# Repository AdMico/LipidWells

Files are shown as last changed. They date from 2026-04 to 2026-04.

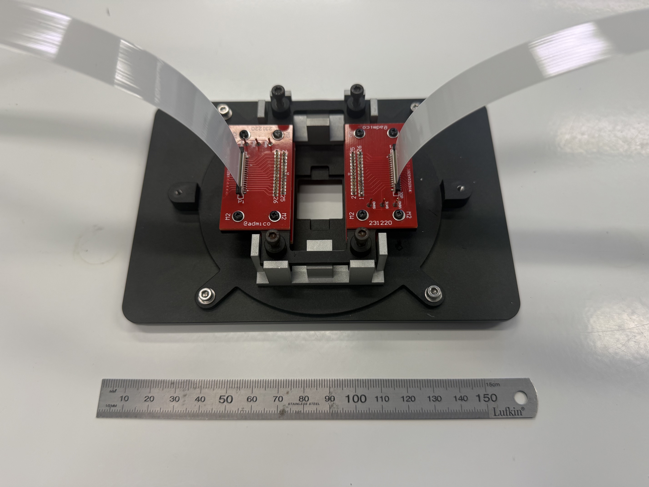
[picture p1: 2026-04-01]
CNC Parts/Stage Parts/Stage_Assy_2.jpeg

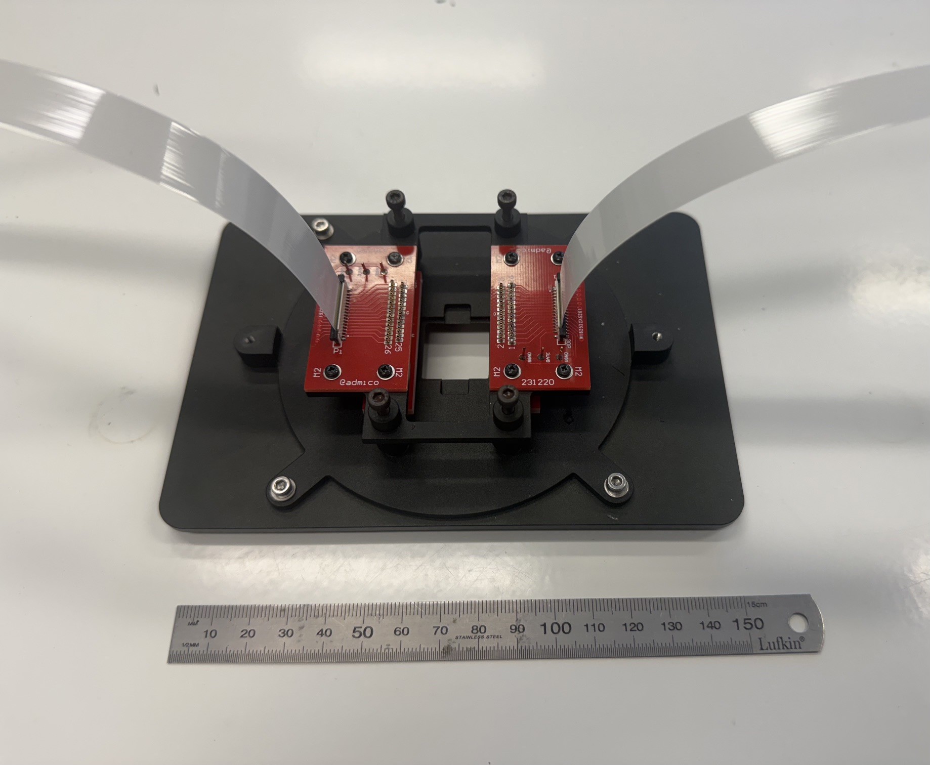
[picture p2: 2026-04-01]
CNC Parts/Stage Parts/Stage_Assy_1.jpeg

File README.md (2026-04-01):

# LipidWells v1.0.0 (Updated 01APR26 APM)

**Written by:** Adam Micolich

**Purpose:** Hardware aspects related to our work on 'Organic Electrochemical Transistor Arrays with Integrated Lipid-Sealed Femtolitre Chambers for Simultaneous Electrical and Optical Detection of Membrane Protein Activity'

## Structure

The top level has three folders -- *CNC Parts*, *PCBs & Schematics* and *Photomasks*.

The *CNC Parts* folder has two sub-folders -- *MUXBox*, which contains all the panels for the multiplexer box, and *Stage Parts*, which has all the various components for mounting a coverslip onto a microscope and making the electrical connections to that coverslip.

The *PCBs & Schematics* folder contains five sub-folders which have the PCB designs, Schematics (as appropriate) and the Gerber file sets for production for the six different PCBs used in this project. It also contains a parts list for all the additional components needed for completing the multiplexer box and associated PCBs.

The *Photomasks* folder contains a PDF file with some extended notes about the respective photomask designs.

The photomask files are hosted as a release due to the large file size involved. The photomask release contains 5 compressed RAR files, which contain the GDSII files for production of the photomasks used in this project, with a download size of 238MB (n.b., some of the files, uncompressed, are nearly 1GB in size due to the huge number of components in the design).

Each of the three folders above has its own `README.md` file with further details regarding the contents of those folders.

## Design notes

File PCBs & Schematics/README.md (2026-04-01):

# LipidWells v1.0.0 (Updated 01APR26 APM)

**Written by:** Adam Micolich

## Contents of the *PCBs & Schematics* folder

There are five folders, the contents of these folders are as follows:

*Drill Board*: This is the PCB for the pair of boards that mount on the bottom of the Pinplate and sit either side of the nodule on the Harwin spring-pin sleeve to set the height of the spring-pins on the Pinplate assembly. There is a PDF file showing the PCB design to actual size, along with a folder containing all the Gerber files needed to have this PCB produced. There is no metal on this board, all it has is drill holes, soldermask and silkscreen.

*MUX Board*: This is the PCB that has all the circuitry for multiplexing the measurement instruments to the devices on the coverslip. I will describe it in more detail in the notes in the next section. There is a photograph of an Assembled MUX Box for reference in building one, along with a PDF file showing the PCB design to actual size, a PDF file showing the schematic diagrams for the circuit, and a folder containing all the Gerber files needed to have this PCB produced. It is a fairly standard two-layer PCB.

*Pin Breakout Board*: This is the PCB that mounts on the top of the Pinplate and which connects the 27 Harwin spring-pins on each side to a corresponding 30-pin ribbon cable. A photograph of a completed version of this PCB, as mounted on the Pinplate, can be found in the *Stage Parts* sub-folder of the *CNC Parts* folder. There is a PDF file showing the PCB design to actual size, a PDF file showing the schematic diagram for the circuit, and a folder containing all the Gerber files needed to have this PCB produced. It is a fairly standard two-layer PCB.

*Sidepanel Board*: This is a PCB that mounts in the left wall of the MUX Box and which acts as a feedthrough for the two 30-pin and one 40-pin ribbon cables from inside to outside the box. There is a PDF file showing the PCB design to actual size, a PDF file showing the schematic diagram for the circuit, and a folder containing all the Gerber files needed to have this PCB produced. It is a fairly standard four-layer PCB, designed to maintain the ground-screening of the left-box wall as much as practicable (in hindsight, perhaps overkill, but interesting to convince myself it could be done should it ever be required for measurements where the signal-to-noise ratio is more difficult that it was in this experiment).

*Test Device Board*: There are actually two PCBs in this folder, which are slight variants of each other. The intention is to make a PCB that can act as a 'dummy device' for testing the electronics/software, without needing to use device coverslips. The 'single' version has a pair of resistors, one for each 'side' of the device, that give a common value on all lines during testing. We invariably always put a 1K, 3K or 10K resistor in here for both positions. The 'multi' version is designed to look more like a real device, in that different lines give slightly different values, and we put a random selection of 2.7K, 3.0K and 3.3K resistors into the 26 SMD resistor positions on this test board. In both cases there is a PDF file showing the PCB design to actual size, and a folder containing all the Gerber files needed to have these PCBs produced. It is a fairly standard two-layer PCB.

We get these PCBs made for us by PCBWay in China.

## Brief discussion of the circuit design aspects for the MUX Box

The schematic for the Mux Board has two sheets, one for the power circuit and one for the signal circuit.

The signal circuit is designed to interface the 60-lines going to the coverslip (54 device lines plus 6 extra lines for ground and gate voltage) to the four BNC connectors that are connected to the analog outputs (AO0/AO1) of the National Instruments USB-6216-BNC and the inputs of the two Femto DLPCA-200 current pre-amplifiers. The switching is performed by a set of four Analog Devices MAX306 16-channel CMOS multiplexer ICs, a pair for each of the 30-pin ribbon cables, that are bit-controlled by the GPIO lines of the Raspberry Pi included in the setup. They are powered by +/-15V rails to minimise the resistance contribution that they make to the measurement lines.

The power circuit is designed to provide the +/-15V supply for the multiplexers. For noise reasons, we elected to do this using a set of four 9V batteries, which provide up to 18V either side of ground. The batteries are split into positive (2 x 9V) and negative (2 x 9V) banks, each of which connect to a DPDT toggle switch on the MUXBox top panel. This switch in the left-hand position connects the batteries to the upper part of the circuit diagram in the schematic, which is a circuit to 'clean-up' the voltage to +/-15V rails. The central position isolates the batteries. The right-hand position connects them to the lower part of the circuit diagram in the schematic, which is a circuit to quickly check the voltage state of the batteries. The green LED and upper SPST momentary switch for each bank (S3/U1/LED3 or S4/U2/LED4) is there to confirm the battery is active and supplying voltage. The red LED and lower SPST momentary switch for each bank is a basic 'low voltage' circuit, which activates the red LED if the battery bank no longer has sufficient overhead (voltage in excess of 15V) to ensure the voltage regulators (IC2/IC3) can supply correctly to the MUX ICs. If battery test gives green LED on and red LED off, then the battery is good for use. If the battery test gives green LED on and red LED on, the battery is low, and if neither LED is on, the battery is probably totally flat (or not connected).

The upper part of the power circuit is broken into two parts. The section on the left is focussed around the DPDT latching relay K1, which will either connect the downstream ICs (IC1, IC2, IC3 and MUXes) to the batteries, or ground all these parts of the circuit to protect them from ESD when the MUXBox is not in use. The relay K1 is driven by GPIO lines from the Raspberry Pi, and is controlled by the PyNE-wells software. Thereafter IC1 is a rail virtual ground IC intended to balance any difference in output voltage of the two banks so that the resulting rails are 'symmetric' about zero, and IC2 and IC3 are positive and negative voltage regulators to step battery voltage down to +/-15V for the MUX ICs.

The Raspberry Pi is connected to the ethernet, and controlled via TCP/IP connection from the PyNE-wells software, which handles all the aspects of the measurement, which includes the switching of the multiplexer connections, the output voltages on AO0 and AO1 of the USB-6216-BNC and the input voltages AI0 and AI1, which return the voltage outputs from the two FEMTO DLPCA-200 current preamplifiers.

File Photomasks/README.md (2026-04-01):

# LipidWells v1.0.0 (Updated 01APR26 APM)

**Written by:** Adam Micolich

## Contents of the *Photomasks* folder

There is only a PDF file `Photomask Details.pdf`, which is an extract from Shuji Kojima's Ph.D. thesis that helps with understanding the design and layout of the mask set.

Due to the large files involved, the photomask GDSII files are available instead as a release asset here: https://github.com/AdMico/LipidWells/releases/tag/Photomasks

The release is a 238MB download, and the files require a suitable GDSII viewer, such as KLayout.

## Contents of the *Photomasks* release

The *Photomasks* release has 5 compressed RAR files containing the GDSII files for producing the photomasks used in this project. The details of the files are as follows:

`LipidWells Mask - Metal.gds`: This contains the first of the three masks used to make the OECT devices. This mask defines all the metallized parts of the device including the source and drain contacts, interconnects, and the various alignment markers for both subsequent photolithography steps as well as positioning of the glass block used to make the flow-cell. It is designed for use with a positive-tone resist such as Microchem's ECI-3012. Contrast = mostly metal, filled areas are transparent.

`LipidWells Mask - Channels_negative.gds`: This contains the second of the three masks used to make the OECT devices. This mask defines the 52 PEDOT:PSS channels on the coverslip. It is designed for a negative-tone resist such as AZ nLOF2020, as we used in our own device fabrication. Contrast = mostly metal, filled areas are transparent.

`LipidWells Mask - Channels_positive.gds`: This contains the second of the three masks used to make the OECT devices. This mask defines the 52 PEDOT:PSS channels on the coverslip. It is designed for positive-tone resist in cases where a negative-tone resist (e.g., AZ nLOF2020) is not available. Our experience has been that PEDOT:PSS channel performance is better if a negative-tone resist is used for patterning of the channels. Contrast = mostly glass, filled areas are metal.

`LipidWells Mask - Wells.gds`: This contains the third of the three masks used to make the OECT devices. This mask defines the hexagonally-close-packed array of 4 micron diameter wells in the active region of the device, as well as two large 'end-zones' for ensuring the fluoropolymer resist is removed at the contact pads for the spring pins. It is designed for use with a positive-tone resist such as Microchem's ECI-3012. Contrast = mostly metal, filled areas are transparent.

`LipidWells Mask - Tokyo.gds`: This is a modified version of the mask above used to make coverslips with only the fluoropolymer layer for more rapid testing of the fluidic aspects of the experiment. It contains only the hexagonally-close-packed array of 4 micron diameter wells in the active region of the device. Contrast = mostly metal, filled areas are transparent.

All masks are 4" soda-lime glass with the contrast specified as above, with chrome side down.

Note: The file `LipidWells Mask - Wells.gds` is extremely large when uncompressed (nearly 1GB in size).

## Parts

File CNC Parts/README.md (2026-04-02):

# LipidWells v1.0.0 (Updated 01APR26 APM)

**Written by:** Adam Micolich

## Contents of the *CNC Parts* folder

This folder has two sub-folders: *MUXBox* and *Stage Parts*

## Contents of the *MUXBox* folder

This folder has CNC-ready STEP files for all the various panels and structures of the multiplexer box (aka MUXBox). The various files are as follows:

`MUXBox_Back_V1-Body.step`: This makes the rear wall of the MUXBox, which supports the four bulkhead BNC connectors and the rear 2 x 9V battery housing.

`MUXBox_Bottom_V1-Body.step`: This makes the baseplate of the MUXBox, with screwpoints for mounting the Mux Board PCB.

`MUXBox_Front_V1-Body.step`: This makes the front wall of the MUXBox, which supports the front 2 x 9V battery housing.

`MUXBox_Left_V1-Body.step`: This makes the left wall of the MUXBox, which supports the sidepanel PCB, which acts as a feedthrough for the two 30-pin and one 40-pin ribbon cables.

`MUXBox_PiHolder_V1-Body.step`: This makes a 'cage' for holding the Raspberry Pi down onto the TopLeft panel of the MUXBox, it is designed to fit the aluminium heatsink specified in the parts list in the *PCBs & Schematics* folder.

`MUXBox_Right_V1-Body.step`: This makes the right wall of the MUXBox, which is a clean panel.

`MUXBox_TopLeft_V2-Body.step`: This makes the top-left lid panel of the MUXBox, which is designed to support the Raspberry pi, which is held in place by the PiHolder mentioned above.

`MUXBox_TopRight_V1-Body.step`: This makes the top-right lid panel of the MUXBox, which supports the two DPDT toggle switches, four SPST momentary switches and four panel-mount LEDs (2 x red, 2 x green) specified in theparts list in the *PCBs & Schematics* folder.

The panels are designed to be machined in aluminium, which is then bead-blasted and anodised, and can be readily done via a company such as PCBway or JLCPCB. I tend to hand-tap the threaded holes myself, both to reduce the CNC cost and ensure the threads are done well.

Any holes in these panels will either be drilled to 3mm diameter, and be clearance holes for an M3 bolt, or be drilled to 2.5mm diameter, ready to be tapped to M3 as a threaded hole for an M3 bolt. It is easy to check which is which using an M3 bolt. ;)

A photograph of a fully assembled MUXBox can be found in the *PCBs & Schematics* folder.

## Contents of the *Stage Parts* folder

This folder has CNC-ready STEP files for all the various components for mounting one of our OECT-coverslips onto a fluorescence microscope. The components are designed for one of two microscope stages. The first is the Marzhauser Wetzlar SCAN IM 120 x 88 stage. The second is the Mad City Labs uS-2308 stage. We use the latter on our current microscope configuration. The various files are as follows:

`Stage_Assy_1.jpeg`: Photograph of the stage assembly with one of the two stages, the Baseplate and the Pinplate shown. The various PCBs and spring-pins are assembled onto the Pinplate.

`Stage_Assy_2.jpeg`: Photograph above with a pair of the Mount Supports in place, which are designed to assist with optimum contact of all 54 spring-pins onto a coverslip.

`Stage_Assy_3.jpeg`: Photograph above with the addition of the five components of the top cover assembled. The two ribbon cables feed through the slots in the cover provided.

`Marzhauser_Stage_Gen4_V1-Body.step`: CNC-ready file for an adaptor plate to mount our Baseplate for supporting the rest of the assembly on a Marzhauser Wetzlar SCAN IM 120 x 100 microscope stage.

`MCL_Stage_Gen4_V1-Body.step`: CNC-ready file for an adaptor plate to mount our Baseplate for supporting the rest of the assembly on a Mad City Labs uS-2308 microscope stage.

`Baseplate_Gen4_V1-Body.step`: CNC-ready file for the Baseplate, which fits into either the Marzhauser stage plate or the Mad City Labs stage plate, and features the cut-out for the coverslip to be positioned into. The four vertical posts are for bolting down the Pinplate assembly.

`Pinplate_Gen4_V1-Body.step`: CNC-ready file for the Pinplate, which holds the various PCBs for mounting the Harwin spring-pins that interface to the 54 device contacts on the coverslip.

`Mount_Support_Gen4_V1a-Body.step`: CNC-ready file for the two Mount Supports, which enable the height of the Pinplate to be set for optimum contact of the spring-pins to the coverslip.

`Coverwall_Gen4_V1-Body.step`: CNC-ready file for the wall of the cover assembly, which bolts onto the Baseplate.

`CoverTopside_Gen4_V1-Body.step`: CNC-ready file for the two edge pieces of the top-plate of the cover assembly, which bolt onto the cover wall.

`CoverTopmid_Gen4_V1-Body.step`: CNC-ready file for the centre piece of the top-plate of the cover assembly, which bolts onto the cover wall.

`CoverTopcent_Gen4_V1-Body`: CNC-ready file for the hole cover for the centre piece listed above. This enables a user to 'peek inside' the cover without needing to disassemble it.

The panels are designed to be machined in aluminium, which is then bead-blasted and anodised (ideally black), and can be readily done via a company such as PCBway or JLCPCB. I tend to hand-tap the threaded holes myself, both to reduce the CNC cost and ensure the threads are done well.

Any holes in these panels will either be drilled to 3mm diameter, and be clearance holes for an M3 bolt, or be drilled to 2.5mm diameter, ready to be tapped to M3 as a threaded hole for an M3 bolt. It is easy to check which is which using an M3 bolt. ;) The one exception is the Pinplate, where there are a set of 1.6mm diameter holes, ready to be tapped to M2, as threaded holes for holding the PCBs in place on this part of the assembly. Use considerable caution in tapping the M2 holes, an M2 tap is very easily broken, especially in deeper holes, whereupon it is basically impossible to get out (trivia: I once had to, from an irreplaceable piece of gold-plated copper for a diode-laser assembly, and we ultimately had to 'cook' it out using a modified arc welding assembly -- the job took 2 days and an uncountable number of swear words before success was finally achieved).

A final note regarding the mount supports. They are intended to be put in place as supports and removed once the pinplate is correctly in place. As such, screw down until the pinplate just makes contact with both mount supports (they should just be unable to be slided out), then loosen each screw just enough for them to be slided with some mild friction, and the height should be correct.

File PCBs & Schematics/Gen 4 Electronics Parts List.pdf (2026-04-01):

Part | Part Number | Manufacturer | Supplier | Qty | Cost | Subtotal

Main Board MUX Gen4

16-channel CMOS Multiplexer IC | MAX306CPI+ | Analog Devices | Mouser | 4 | $35.860 | $143.44
28-pin 2.54mm pitch DIL Socket | A 28-LC-TT | Assmann WSW | RS Components | 4 | $0.774 | $3.10
30-pin ribbon cable connector | 687330124422 | Wurth Electronik | Mouser | 2 | $3.660 | $7.32
40-pin ribbon cable connector | 687340124422 | Wurth Electronik | Mouser | 1 | $4.290 | $4.29
Small Signal Diode (D1/D2) | MRA4004T3G | Onsemi | Mouser | 2 | $0.326 | $0.65
1.2K 1% Resistor (R11/R12) | CR0805-FX-1201ELF | Bourns | Mouser | 2 | $0.148 | $0.30
NPN Bipolar Transistor (Q1-Q4) | BC547B | Onsemi | Mouser | 4 | $0.192 | $0.77
20mA LED Driver (U1/U2) | CL2K4-G | Microchip Technology | Mouser | 2 | $1.150 | $2.30
DPDT Relay (K1) | TQ2SS-L2-5V | Panasonic | Mouser | 1 | $6.700 | $6.70
Virtual Ground Rail (IC1) | TLE2426CD | Texas Instruments | Mouser | 1 | $4.600 | $4.60
Positive Voltage Regulator (IC2) | LM78L15ACMX/NOPB | Texas Instruments | Mouser | 1 | $1.050 | $1.05
Negative Voltage Regulator (IC3) | LM79L15ACMX/NOPB | Texas Instruments | Mouser | 1 | $1.150 | $1.15
Voltage Reference (IC4/IC5) | TL431ACD | Texas Instruments | Mouser | 2 | $1.150 | $2.30
220K 1% Resistor (R1/R6) | WCR0805-220KFI | Welwyn | Mouser | 2 | $0.192 | $0.38
40.2K 1% Resistor (R2/R7) | CR0805-FX-4022ELF | Bourns | Mouser | 2 | $0.148 | $0.30
2.2K 1% Resistor (R3/R8) | WCR0805-2K2FI | Welwyn | Mouser | 2 | $0.192 | $0.38
47K 1% Resistor (R4/R9) | WCR0805-47KFI | Welwyn | Mouser | 2 | $0.192 | $0.38
1K 1% Resistor R5/R10 | WCR0805-1K0FA | Welwyn | Mouser | 2 | $0.237 | $0.47

Side Feedthrough Board

30-pin ribbon cable connector | 687330124422 | Wurth Electronik | Mouser | 4 | $3.660 | $14.64
40-pin ribbon cable connector | 687340124422 | Wurth Electronik | Mouser | 2 | $4.290 | $8.58

Other MUX Gen4 Parts
Bulkhead BNC Connector | CONBNC004 | TE Connectivity | Mouser | 4 | $3.240 | $12.96
Flat 30-pin ribbon cable 7" | FJH-30-R-07.00-4 | Samtec | Mouser | 2 | $8.730 | $17.46
Flat 40-pin ribbon cable 6.5" | FJH-40-D-06.50-4 | Samtec | Mouser | 1 | $9.810 | $9.81
Red Panelmount LED (LED1/2) | WP1533AA/ID-W152 | Kingbright | Mouser | 2 | $4.740 | $9.48
Green Panelmount LED (LED3/4) | WP1533AA/GD-W152 | Kingbright | Mouser | 2 | $4.650 | $9.30
9V Battery Holders | BX0026 | Bulgin | Mouser | 2 | $59.850 | $119.70
Red Mini. Pushbutton SPST (S3-S6) | SP0710 | Jaycar | Jaycar | 4 | $1.950 | $7.80
DPDT Toggle Switch (S1/S2) | 472131010111 | Wurth Electronik | Mouser | 2 | $10.430 | $20.86

Pin Breakout Parts (Both boards)
Harwin Crimp Sleeve | S13-503 | Harwin | Mouser | 54 | $2.650 | $143.10
Harwin 1.27mm Spring Probe | P13-4023 | Harwin | Mouser | 54 | $6.130 | $331.02

Test Device PCBs
2.7K 1% Resistor | WCR0805-2K7FI | Welwyn | Mouser | 10 | $0.192 | $1.92
3.0K 1% Resistor | CR0805-JW-302ELF | Bourns | Mouser | 10 | $0.163 | $1.63
3.3K 5% Resistor | CR0805-JW-332ELF | Bourns | Mouser | 10 | $0.148 | $1.48
1K 1% Resistor | WCR0805-1K0FA | Welwyn | Mouser | 2 | $0.237 | $0.47

Peripherals
Raspberry Pi 4B 8GB | CE06974 | Raspberry Pi | Core Electronics | 1 | $196.960 | $196.96
Al Heatsink Case | CE06583 | Raspberry Pi | Core Electronics | 1 | $14.800 | $14.80
Raspberry Pi 4 Power Supply | CE06427 | Raspberry Pi | Core Electronics | 1 | $11.900 | $11.90
40-Pin GPIO to ribbon connector | ADA4905 | Adafruit | Core Electronics | 1 | $6.950 | $6.95
40-pin GPIO ribbon cable | ADA4933 | Adafruit | Core Electronics | 1 | $1.910 | $1.91
| | | | | TOTAL | $1,122.62
Prices at 1/4/26

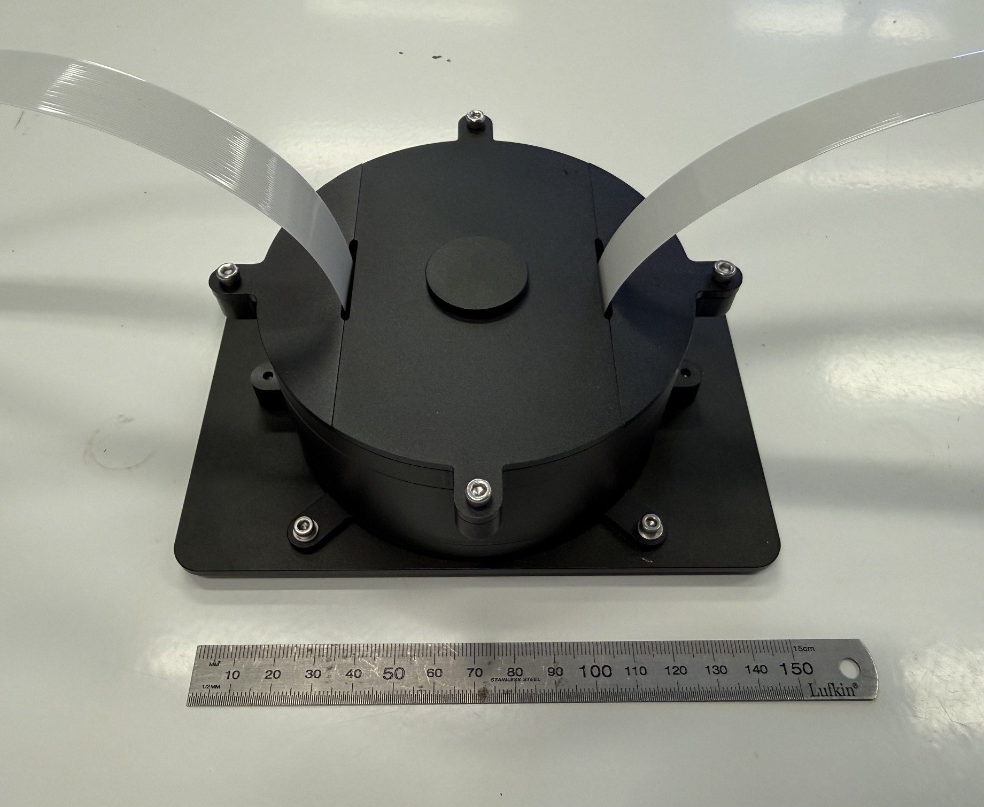
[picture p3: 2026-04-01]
CNC Parts/Stage Parts/Stage_Assy_3.jpeg

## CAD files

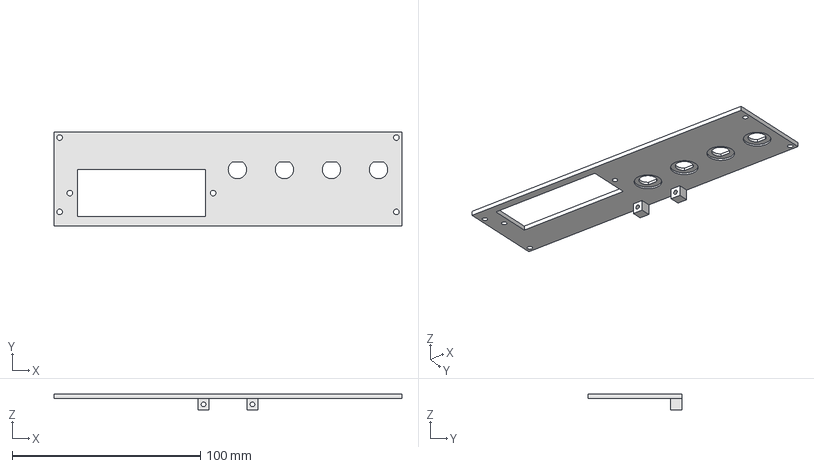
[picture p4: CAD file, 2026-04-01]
CNC Parts/MUXBox/MUXBox_Back_V1-Body.step
185.0 x 50.0 x 8.50 mm

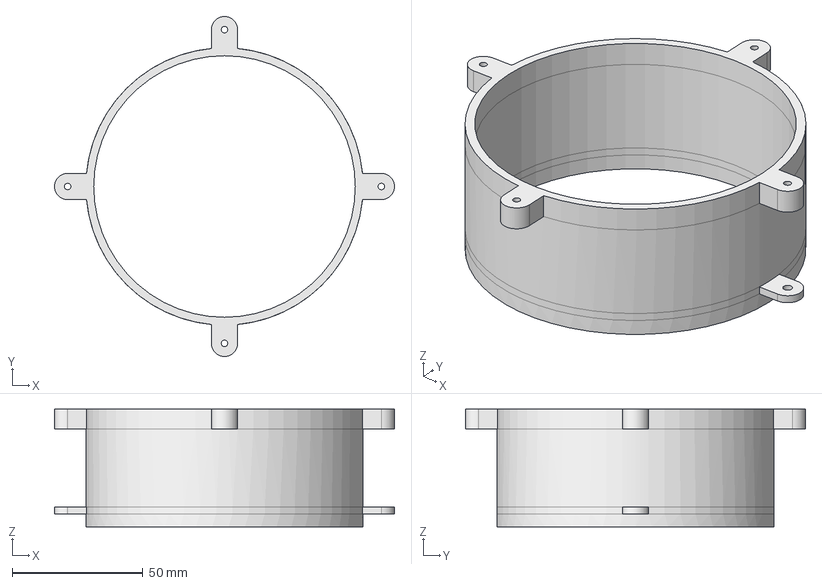
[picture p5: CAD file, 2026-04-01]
CNC Parts/Stage Parts/Coverwall_Gen4_V1-Body.step
130.0 x 130.0 x 45.0 mm

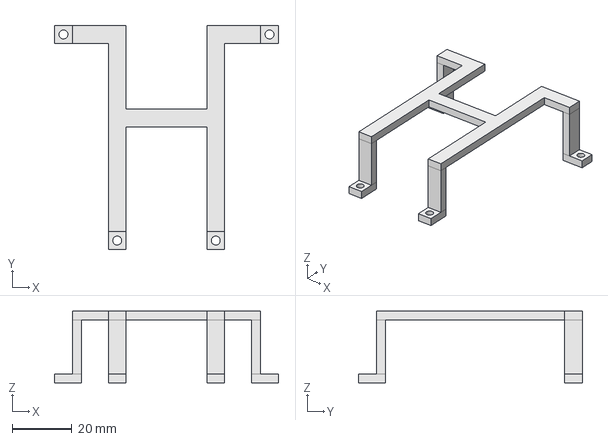
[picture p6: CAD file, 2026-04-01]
CNC Parts/MUXBox/MUXBox_PiHolder_V1-Body.step
75.0 x 75.0 x 24.0 mm

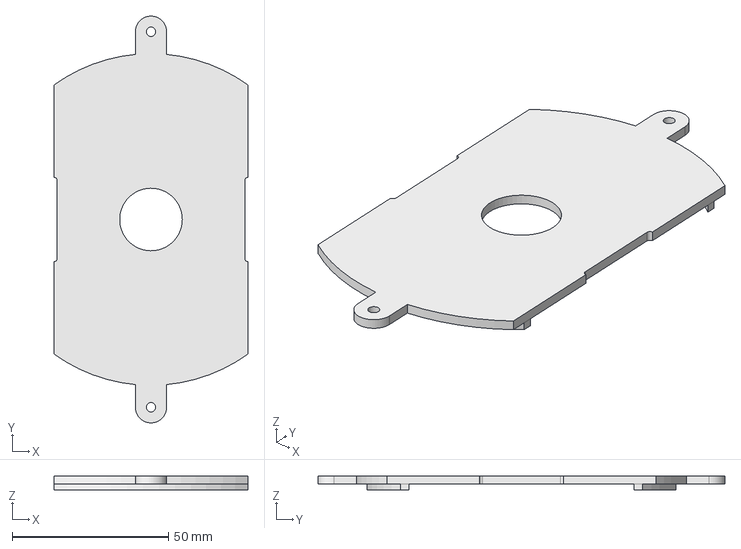
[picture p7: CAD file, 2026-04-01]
CNC Parts/Stage Parts/CoverTopmid_Gen4_V1-Body.step
62.0 x 130.0 x 4.50 mm

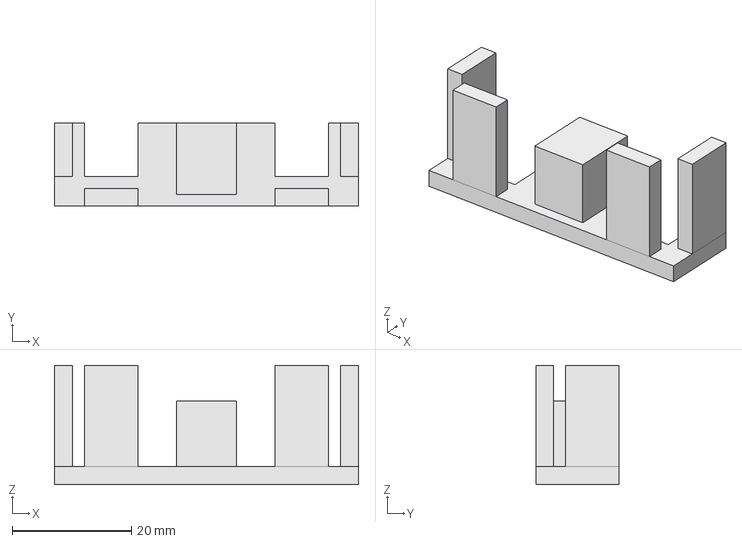
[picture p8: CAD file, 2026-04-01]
CNC Parts/Stage Parts/Mount_Support_Gen4_V1a-Body.step
51.0 x 14.0 x 20.0 mm

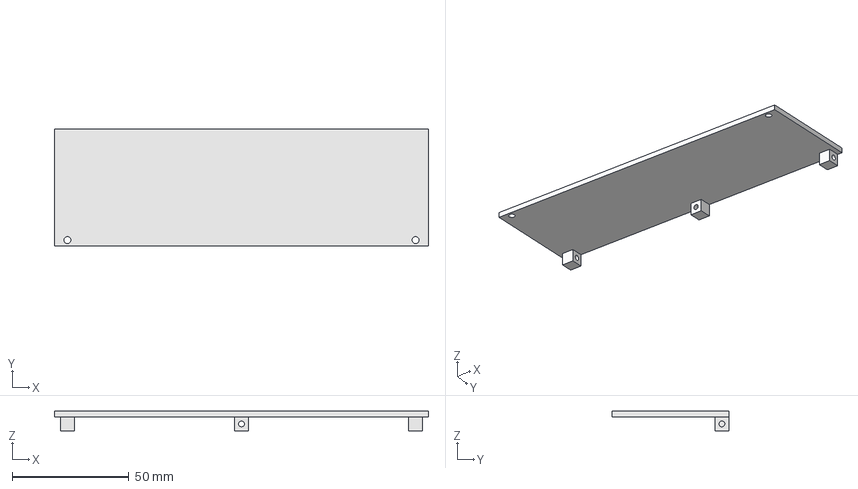
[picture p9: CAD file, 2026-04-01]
CNC Parts/MUXBox/MUXBox_Right_V1-Body.step
160.0 x 50.0 x 8.50 mm

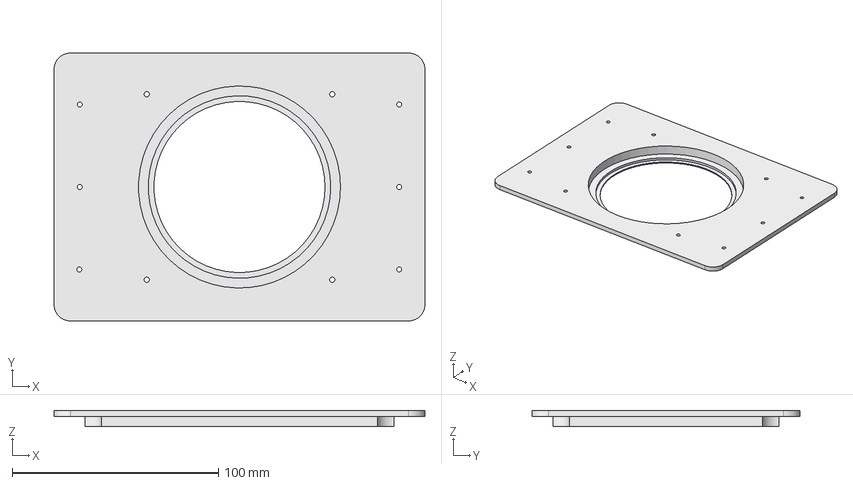
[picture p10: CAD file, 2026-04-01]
CNC Parts/Stage Parts/MCL_Stage_Gen4_V1-Body.step
180.0 x 130.0 x 8.00 mm

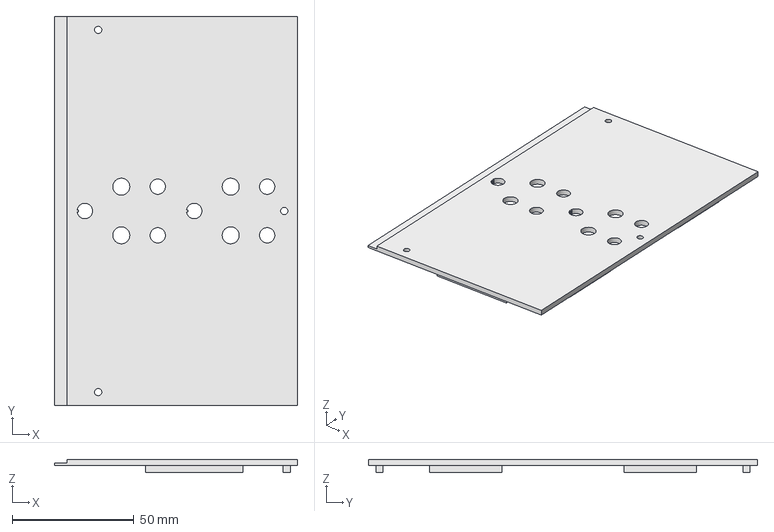
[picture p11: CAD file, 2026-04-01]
CNC Parts/MUXBox/MUXBox_TopRight_V1-Body.step
100.0 x 160.0 x 5.50 mm

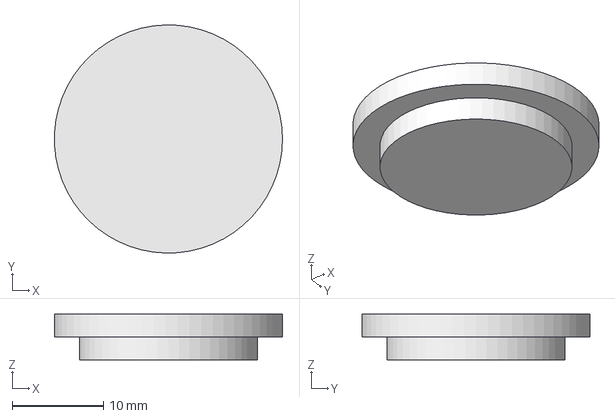
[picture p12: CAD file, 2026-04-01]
CNC Parts/Stage Parts/CoverTopcent_Gen4_V1-Body.step
25.0 x 25.0 x 5.00 mm

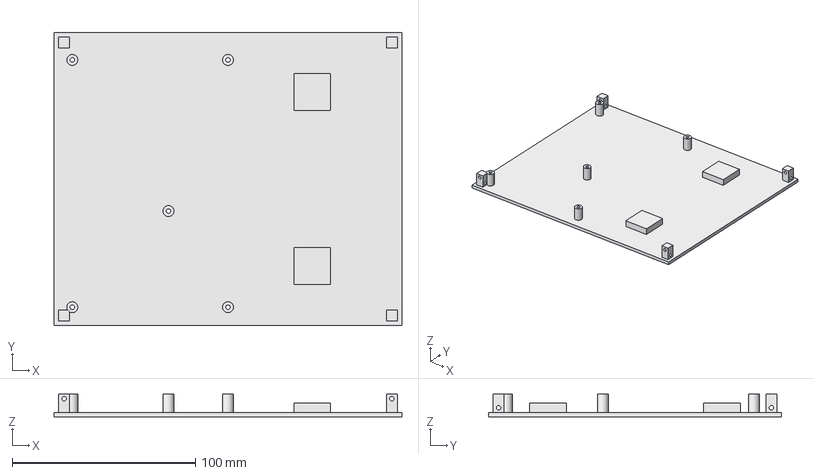
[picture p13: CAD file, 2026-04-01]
CNC Parts/MUXBox/MUXBox_Bottom_V1-Body.step
190.0 x 160.0 x 12.5 mm

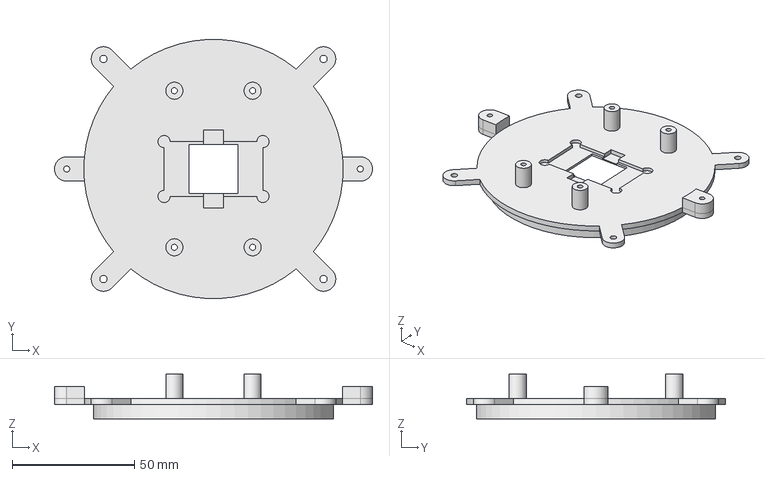
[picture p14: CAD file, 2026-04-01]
CNC Parts/Stage Parts/Baseplate_Gen4_V1-Body.step
130.0 x 105.9 x 18.3 mm

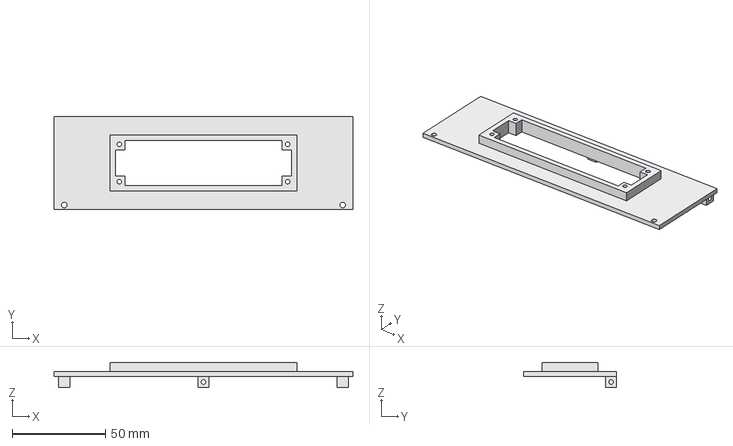
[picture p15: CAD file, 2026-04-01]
CNC Parts/MUXBox/MUXBox_Left_V1-Body.step
160.0 x 50.0 x 13.5 mm

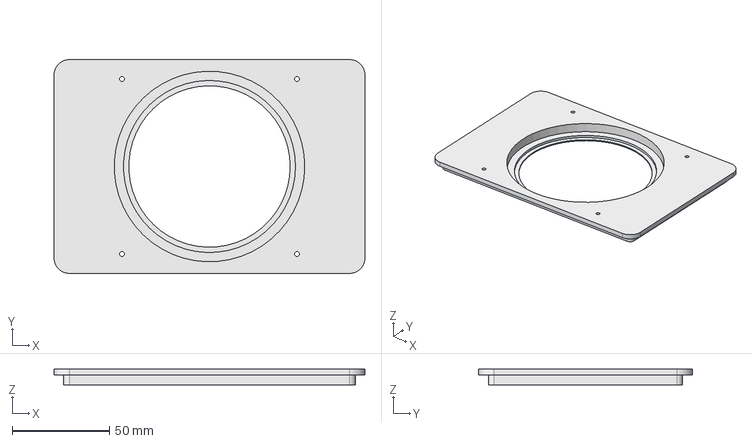
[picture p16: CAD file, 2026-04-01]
CNC Parts/Stage Parts/Marzhauser_Stage_Gen4_V1-Body.step
160.0 x 110.0 x 8.00 mm

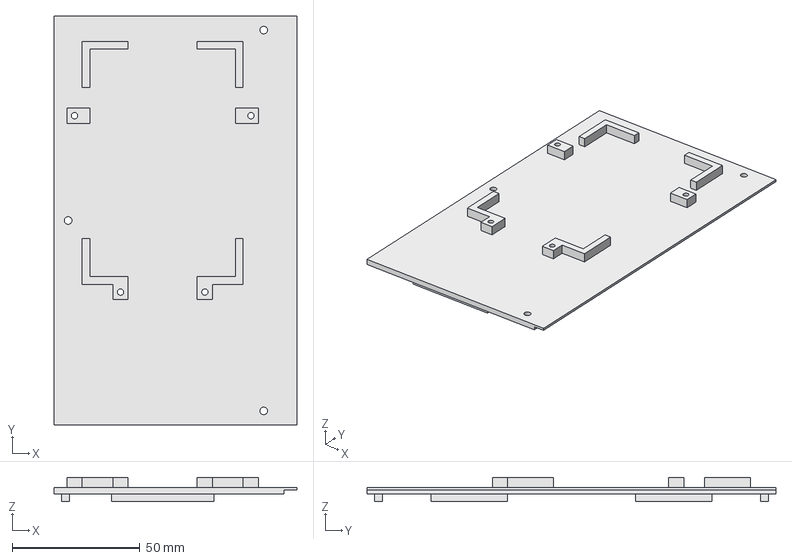
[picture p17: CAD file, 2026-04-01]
CNC Parts/MUXBox/MUXBox_TopLeft_V2-Body.step
95.0 x 160.0 x 9.50 mm

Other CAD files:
CNC Parts/MUXBox/MUXBox_Front_V1-Body.step
CNC Parts/Stage Parts/CoverTopside_Gen4_V1-Body.step
CNC Parts/Stage Parts/Pinplate_Gen4_V1-Body.step

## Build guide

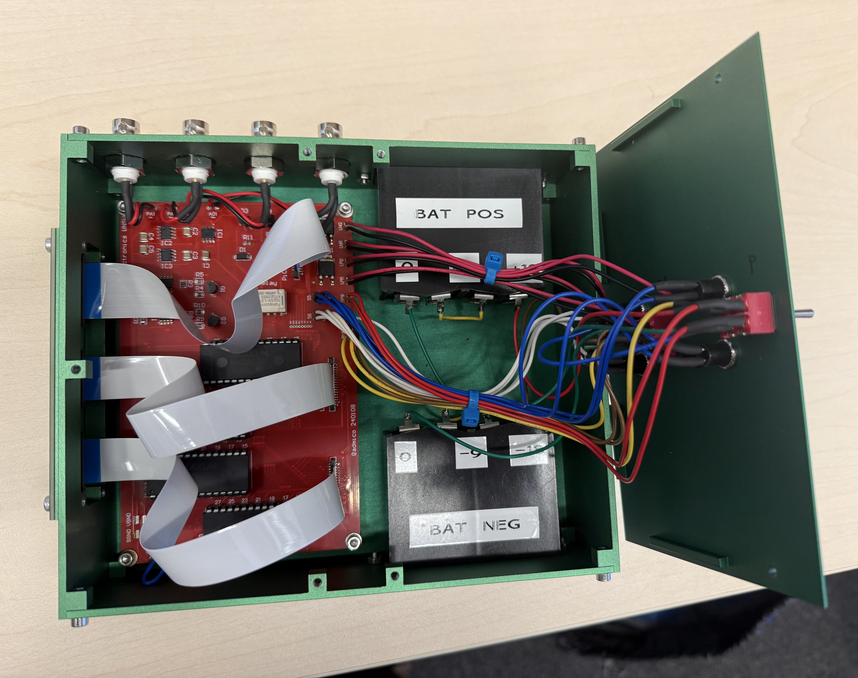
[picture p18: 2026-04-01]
PCBs & Schematics/MUX Board/Assembled MUX Gen4 Box.jpeg

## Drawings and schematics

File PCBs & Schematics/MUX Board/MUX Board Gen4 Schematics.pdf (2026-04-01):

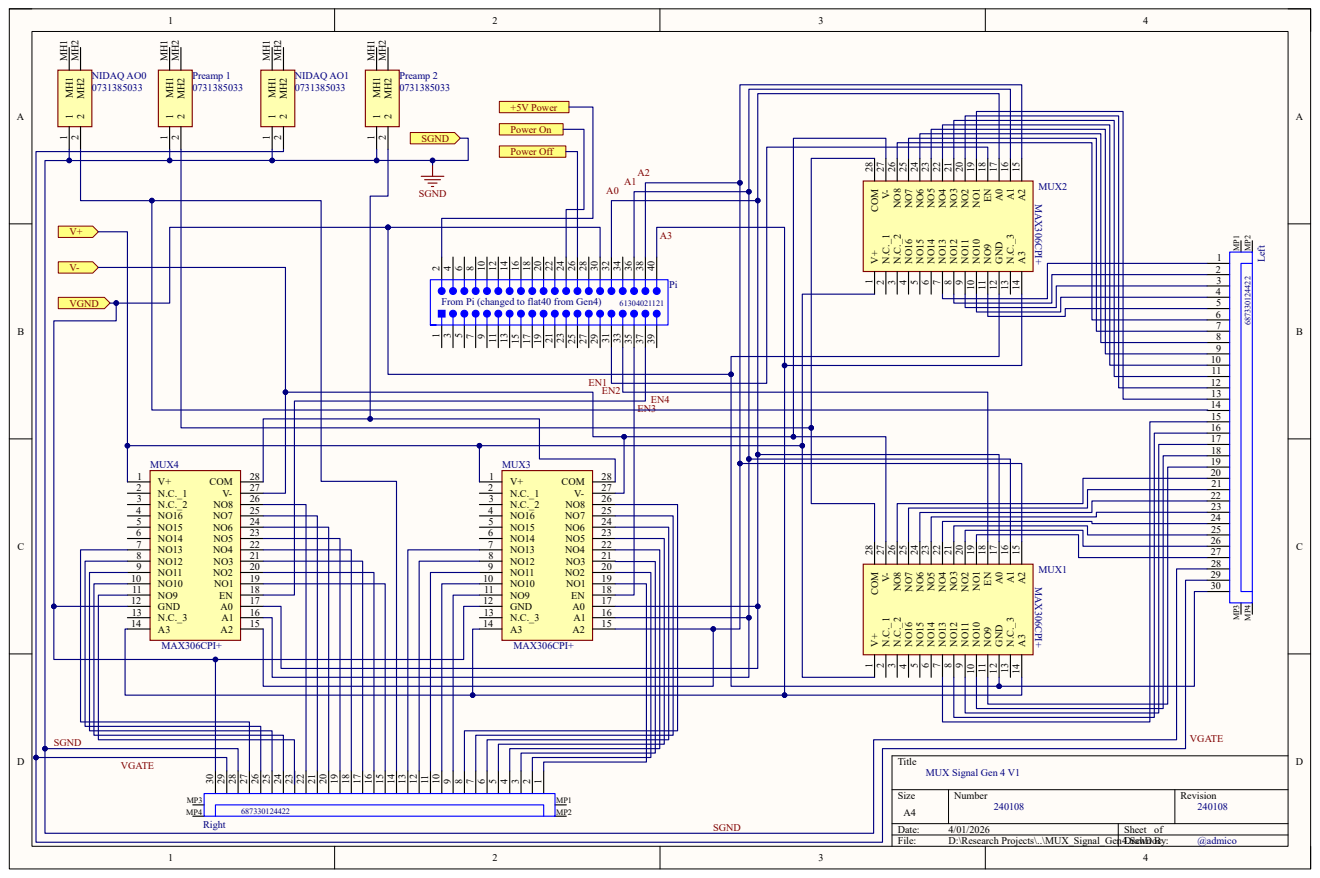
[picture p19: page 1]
V+ 1 N.C._1 2 N.C._2 3 NO16 4 NO15 5 NO14 6 NO13 7 NO12 8 NO11 9 NO10 10 NO9 11 GND 12 N.C._3 13 A3 14; COM; MUX3; MAX306CPI+; MUX4; Right; 2 MH1 MH1 MH2 MH2 Preamp 1 0731385033; 2 MH1 MH1 MH2 MH2 NIDAQ AO0 0731385033; SGND; GND 12; COM 28; A1 16 A2 15 MUX2; A1 16 A2 15 MUX1; Left; 2 MH1 MH1 MH2 MH2 NIDAQ AO1 0731385033; 2 MH1 MH1 MH2 MH2 Preamp 2 0731385033; VGND; VGATE; +5V Power; Power On; Power Off

39 40 Pi From Pi (changed to flat40 from Gen4) 61304021121

Title
MUX Signal Gen 4 V1

Size A4 | Number 240108 | Revision 240108

Date: 4/01/2026 | Sheet of
File: D:\Research Projects\..\MUX_Signal_Gen4.SchDoc Drawn By: | @admico

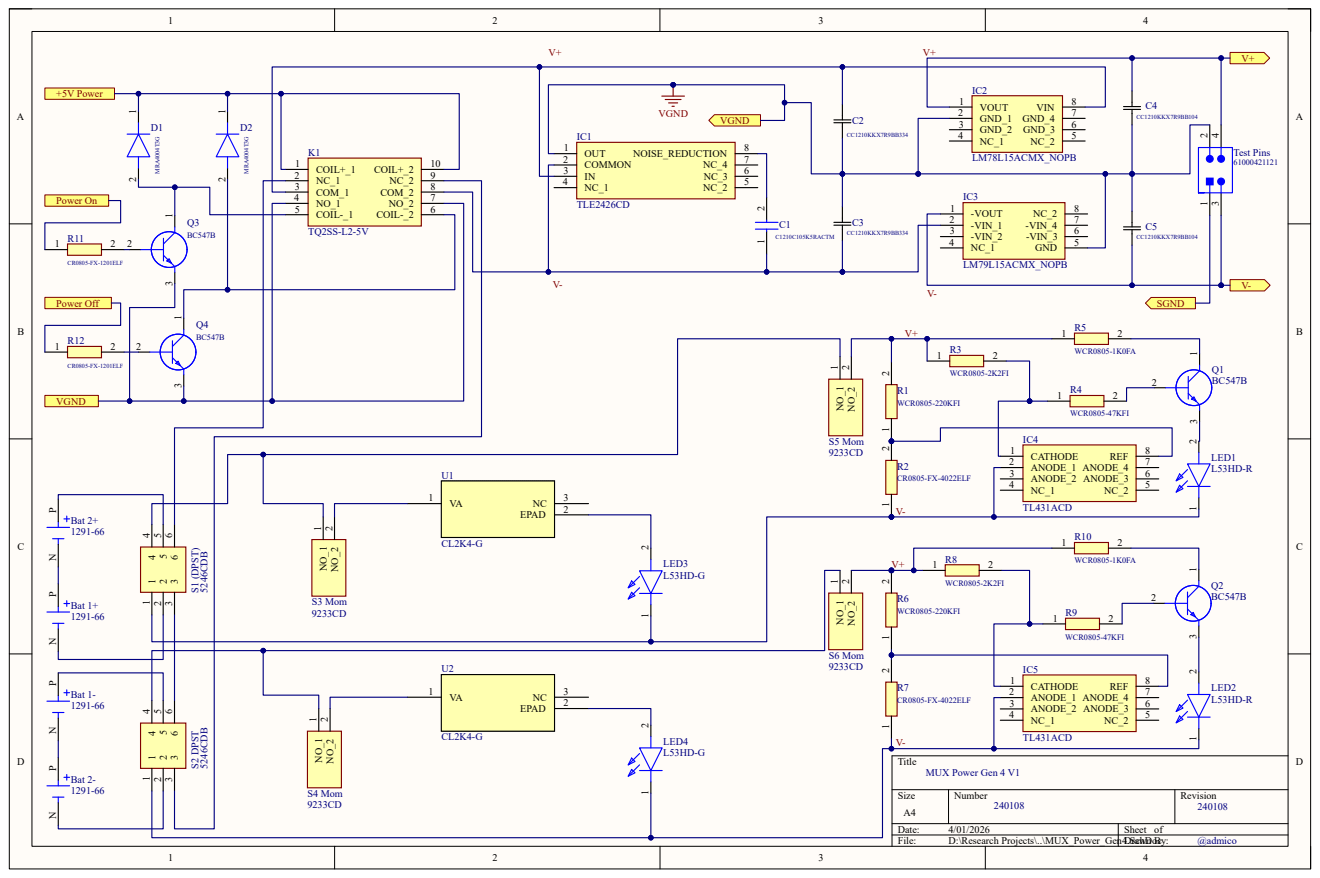
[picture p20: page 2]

Size A4 | Number 240108 | Revision 240108

Date: 4/01/2026 | Sheet of
File: D:\Research Projects\..\MUX_Power_Gen4.SchDoc Drawn By: | @admico

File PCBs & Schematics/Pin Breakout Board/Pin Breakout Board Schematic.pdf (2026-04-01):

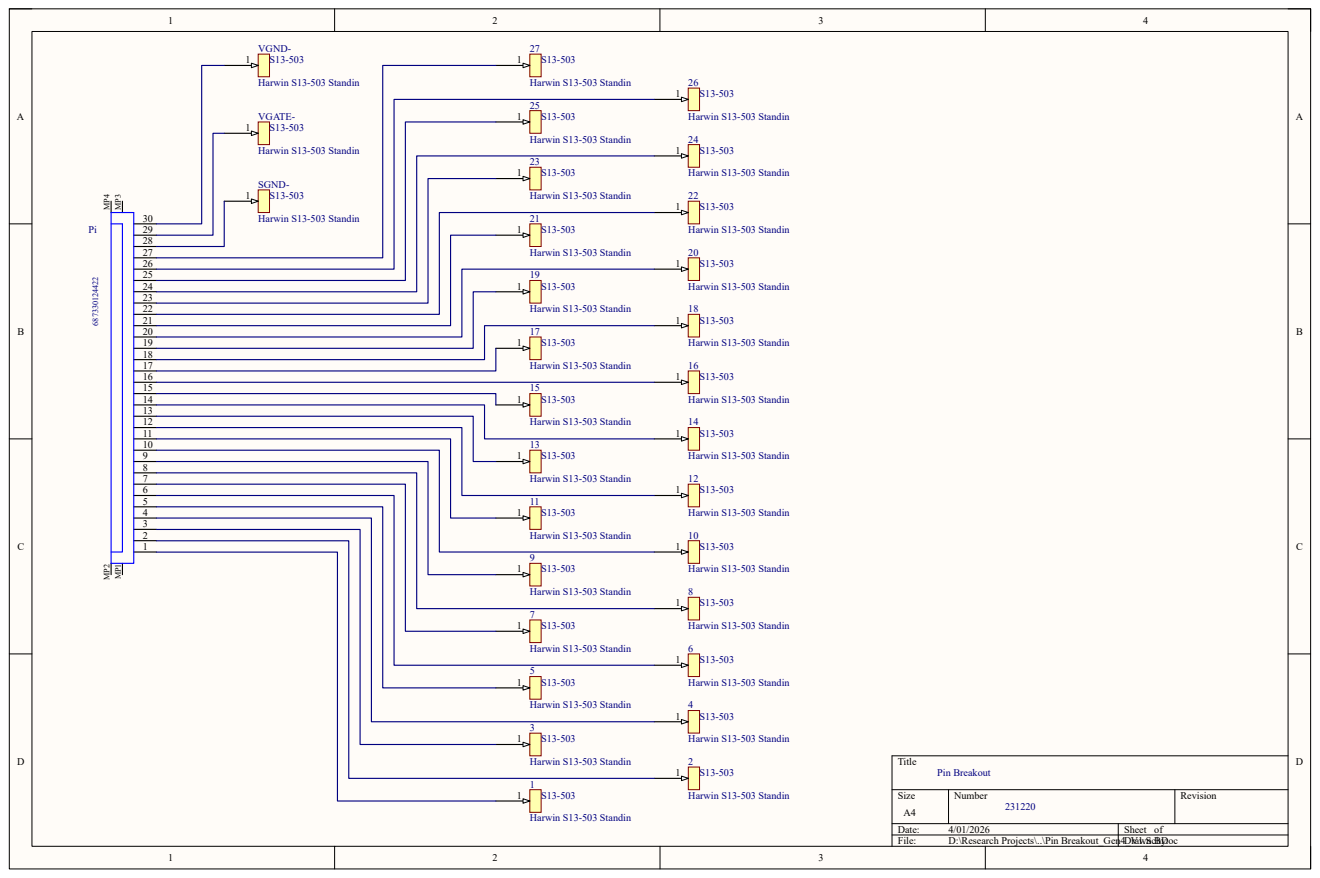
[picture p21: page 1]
Title; Harwin S13-503 Standin; SGND-; VGATE-; VGND-; Pin Breakout

Size A4 | Number 231220 | Revision

Date: 4/01/2026 | Sheet of
File: D:\Research Projects\..\Pin Breakout_Gen4_V1.SchDoc Drawn By:

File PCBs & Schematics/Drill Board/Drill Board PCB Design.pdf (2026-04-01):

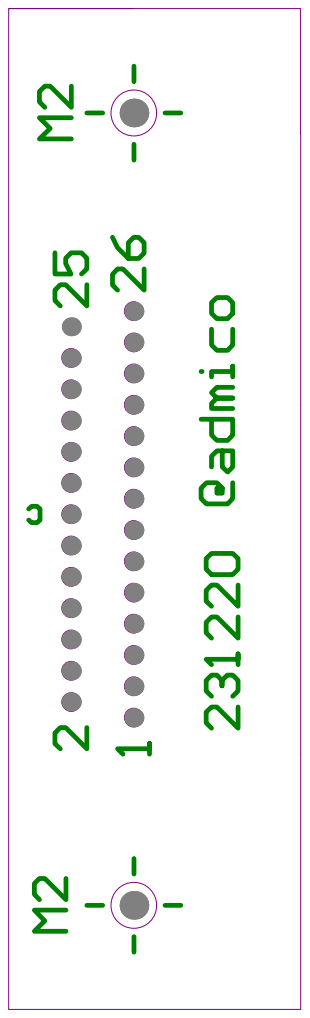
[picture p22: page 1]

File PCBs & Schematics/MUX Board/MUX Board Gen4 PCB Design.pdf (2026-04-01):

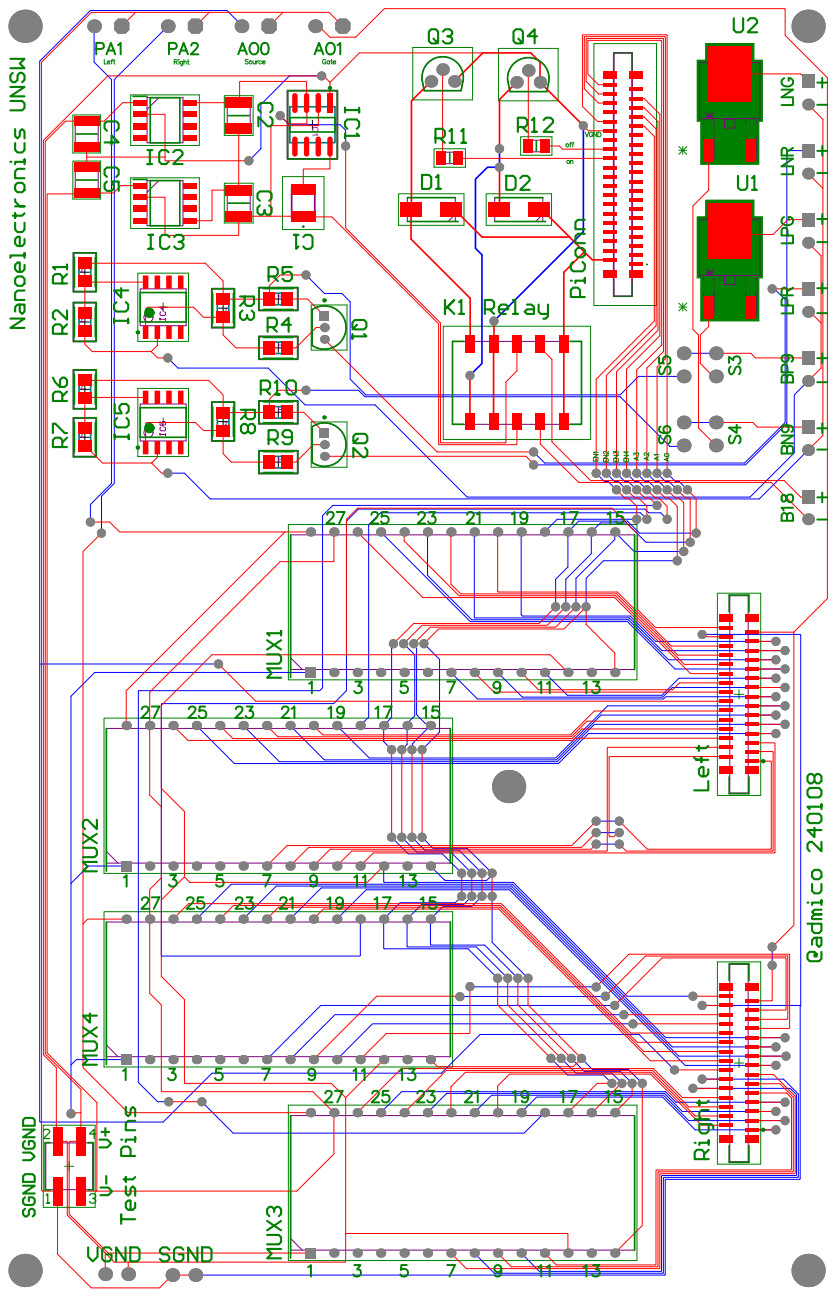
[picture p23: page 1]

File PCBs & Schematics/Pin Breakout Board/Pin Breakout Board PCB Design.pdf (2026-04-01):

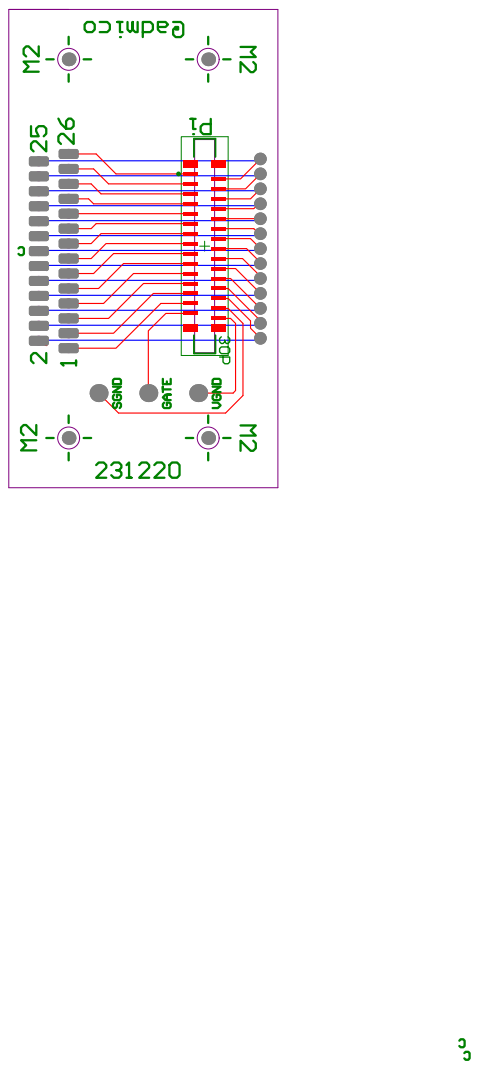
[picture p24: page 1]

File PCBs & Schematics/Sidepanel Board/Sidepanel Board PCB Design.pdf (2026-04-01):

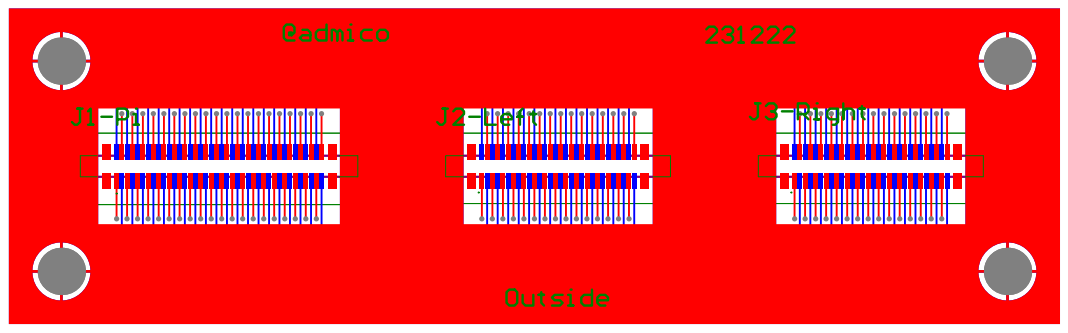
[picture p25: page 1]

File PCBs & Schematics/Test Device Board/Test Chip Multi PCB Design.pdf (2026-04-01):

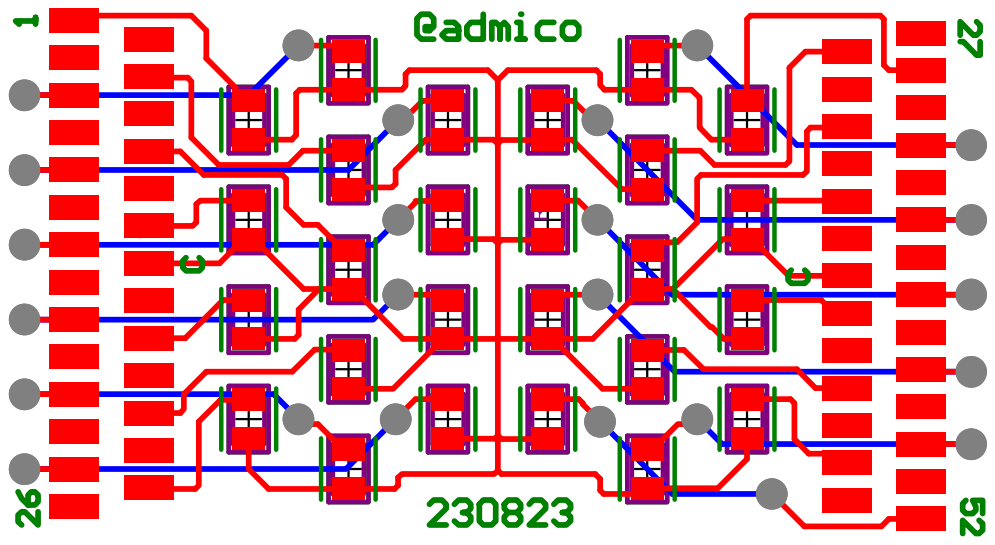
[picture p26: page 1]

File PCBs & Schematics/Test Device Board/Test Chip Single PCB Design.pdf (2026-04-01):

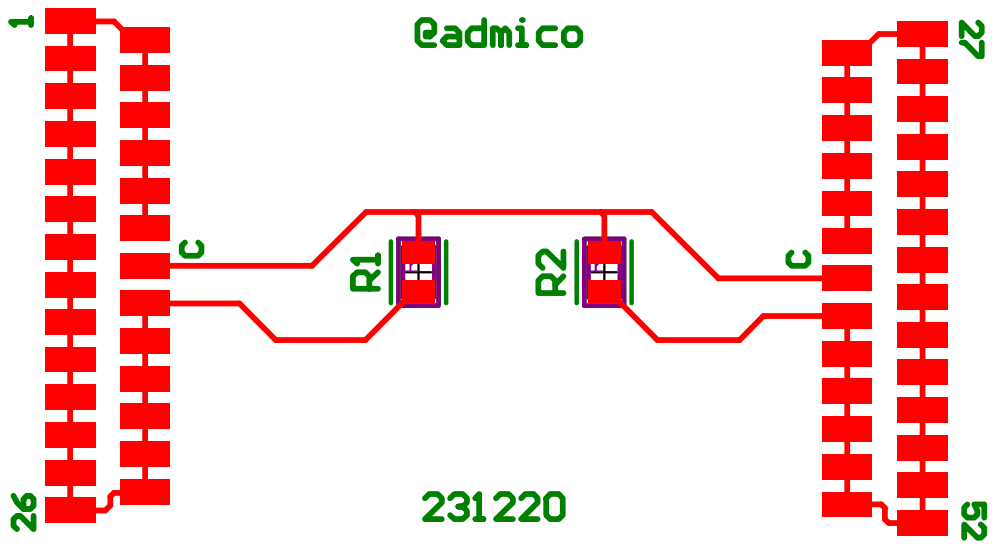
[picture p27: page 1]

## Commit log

2026-04-01 Initial Upload
    Initial Upload
    [Baseplate_Gen4_V1-Body.step, CoverTopcent_Gen3_V1-Body.step, CoverTopmid_Gen3_V1-Body.step, CoverTopside_Gen3_V1-Body.step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]
2026-04-01 Create Assembled MUX Gen4 Box.jpeg
2026-04-01 Update README.md in PCBs & Schematics folder
2026-04-01 Update README.md for PCBs & Schematics folder
2026-04-01 Update after Readme edits
    [CoverTopcent_Gen4_V1-Body.step, CoverTopmid_Gen4_V1-Body.step, CoverTopside_Gen4_V1-Body.step, Coverwall_Gen4_V1-Body.step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]
2026-04-02 Update README.md -- Stage update
